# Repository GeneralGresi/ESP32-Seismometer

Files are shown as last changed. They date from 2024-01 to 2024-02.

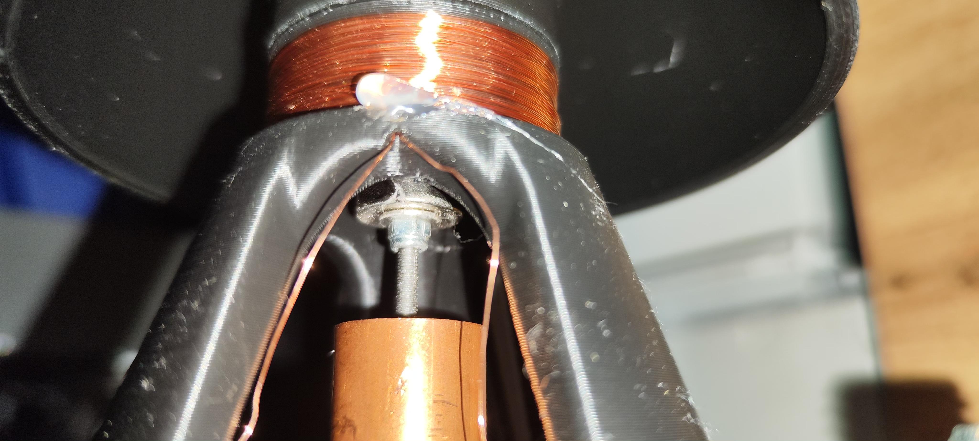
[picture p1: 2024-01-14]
Pictures/Magnet Base.jpg

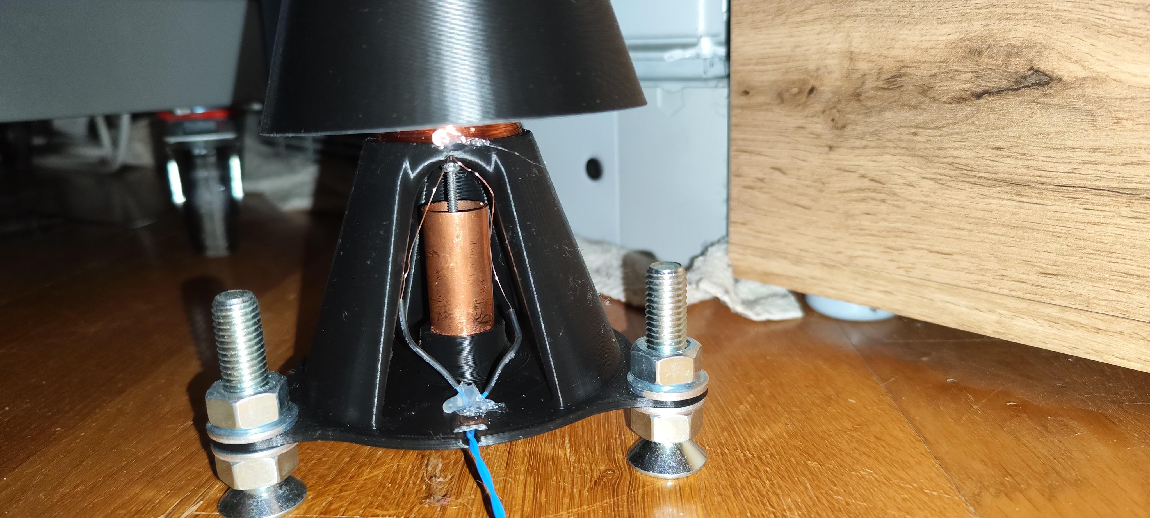
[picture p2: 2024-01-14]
Pictures/Magnet Base 2.jpg

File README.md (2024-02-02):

This is a DIY Project for building a simple 3D Printable Seismometer, interfacing to InfluxDB/Grafana via an ESP32.

POC:
Recorded a quake, Richter 4.5, about 130km away

https://www.zamg.ac.at/cms/de/geophysik/erdbeben/aktuelle-erdbeben/karten-und-listen/bebendetails/austria/quakes/evid53139145



The main principal is a magnet on a spring. Each "movement" will cause the magnet to swing, therefore inducing a voltage/current in a coil. 


Schematic Seismometer Stand

As the coil itself would not produce much voltage, we have to amplify this voltage. Depending on the strength of a potential earthquake I was unsure which gain is needed.
Therefore I disigned a multi gain op-amp circuit utilizing high precision LN1677 chips. This implements a gain of 10, 100 and 1000. Each gain is funneled seperately to an Analog Input pin on the ESP32.



The op-amp circuit works as follows: Via a voltage devider we create a median voltage between 0 and 3.3V. The coil is connected directly to this voltage devider, as well as to each inverting input of the op amps.
The difference between the median voltage and the input voltage is then amplified by the respective gain, creating a bigger offset value.

Circuit

The ESP32 reads these values, funnels it through a software low-pass filter of 35 Hz (Earth Quakes are usually between 0.1Hz and 30Hz, I also want to filter out the mains voltage of 50Hz, therefore everything below 35Hz is considered acceptable).
As due to unknown reasons (at least for me), we are not perfectly centered to 0 during no movement of the magnet, therefore we take the average of 500 readings (at a sample rate of about 200Hz/~5000ys delay between reading we have an average of 2,5 Seconds). 
This average then is used to move the raw median value to 0. This approach works pretty well.

I mapped the min and max values from -1000 to 1000 for each input. If we overshoot this value at for example the X1000 value, we use the next-lowest beeing X100, and multiply it by 10, to get consistent values to InfluxDB.
A value of 300 on the X100 Gain Input will be transmited as 3000 to InfluxDB. The same applies for X10/X100.
The final value then get's put into a queue, as well as the current timestamp. 

I use NTP for time synchronisation - we can't use the server timestamp, as we never send data right away.
The values are first put into a Queue and send the to InfluxDB in batches by a seperate thread.
This ensured, the wifi send command doesn't interrupt further reading of new values. 

For winding of the coil, there is a separate script for an Arduino Uno (or whatever microcontroller), which uses magnets and a magnet switch to register each rotation and display it on an LCD. Serial Printing the value would also be an option though.
The magnet switch is connected to a cordless drill, the Base is connected via a Metric Screw, and a 3D printed adapter. Use about 300-500 windings. More windings = Increased sensitivity.
CoilWinding

The magnetic part of the seismometer looks as follows: It uses 15mm and 10mm Magnets, as well as a 5mm steel threaded rod and some fixation rings with setscrews.
Magnet Part
Magnet on Spring

The upper two magnets are inducing the voltage into the coil, the bottom two are for dampening the movement. Therefore a copper tube with 20mm (inner 18mm) in diameter is inserted into the base.
Base Prototype

Due to eddy currents, the copper tube acts like a dampener/break for the magnets, slowing them down. This greatly shortens swinging after an event.
Using the 3D printed Setscrew, the contraption is lowered into the base, making sure the bigger magnets are perfectly centered within the coil, and the dampening magnets are reaching the copper tube. 
They should be at least 1cm within the tube, in order to have the dampening work even when a swinging motion has the contraption in it's highest position.
This can take some time fiddling around, testing longer or shorter steel rods, and cutting the spring to length. I can't give you any exact numbers, as this depends greatly on the weight of each component.

Magnet Base

Once finished it should look like that:
Magnet Base 2

On the Edges there are M16 Screws and nuts to level the Seismometer. For increased sensitivity, steel threaded Rods which are hammered into the ground can be used.  
For leveling, take a look into each side hole of the base, and make sure the magent contraption is perfectly centered. If it is off, or even worse, it rubs against the copper tube, the reading will be absolutely garbage.

Once you are finished, carefully slíde over and scrow on the conver over the base. This prevents air movement to cause any distortion.

Regarding the circuit:
I enhoused it in a plastic box, with a buck converter which is creating a steady 5V, a Li-Ion module to serve as UPS, as well as some additional capacitors and a choke to smooth the input voltage even more.

Circuit Box

End result:


Why the aluminium foil one may ask? I don't think it helps much, but the intention was the keep external electical signals away from the coil... 

As the ESP32 sends it's data directly to an InfluxDB Instance, we can read out the values via Grafana very easily. Just make sure the timespan is not too big, as we have about 12k values each minute.

On Idle:
Screenshot Grafana Idle

Walking by:


Zoomed in:


As you can see, the dampening can be improved still, however, I consider this a great success.

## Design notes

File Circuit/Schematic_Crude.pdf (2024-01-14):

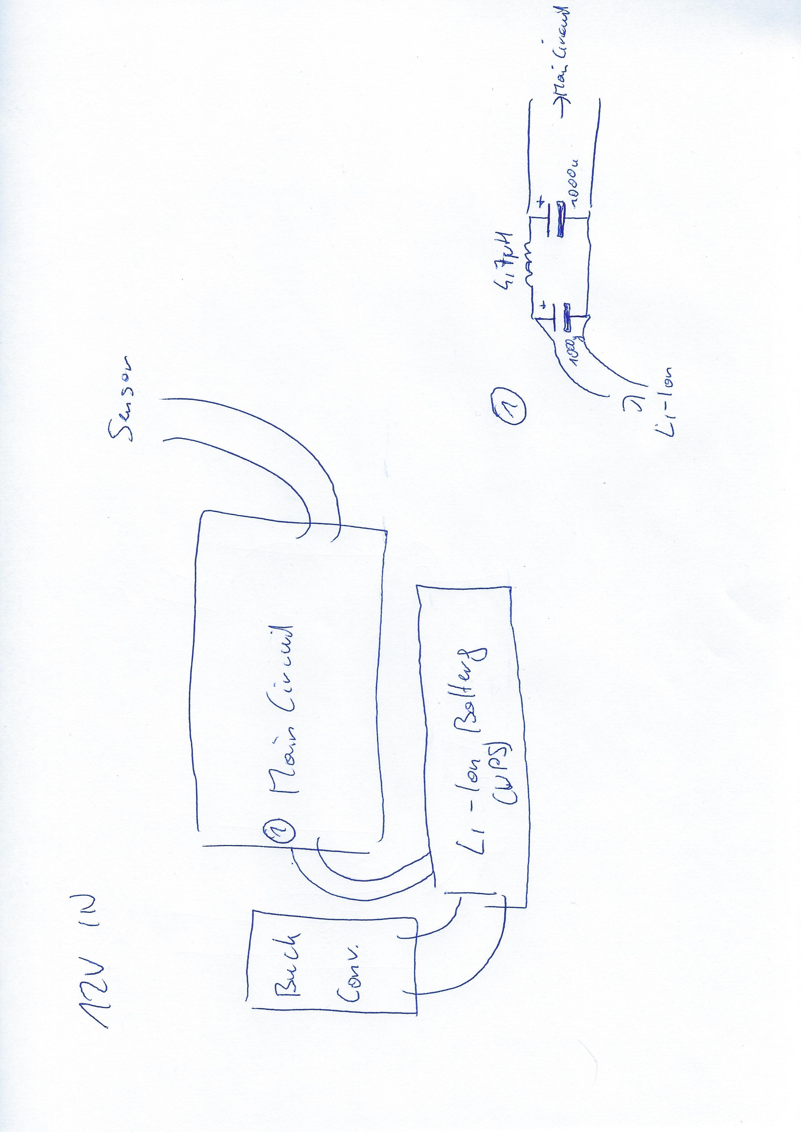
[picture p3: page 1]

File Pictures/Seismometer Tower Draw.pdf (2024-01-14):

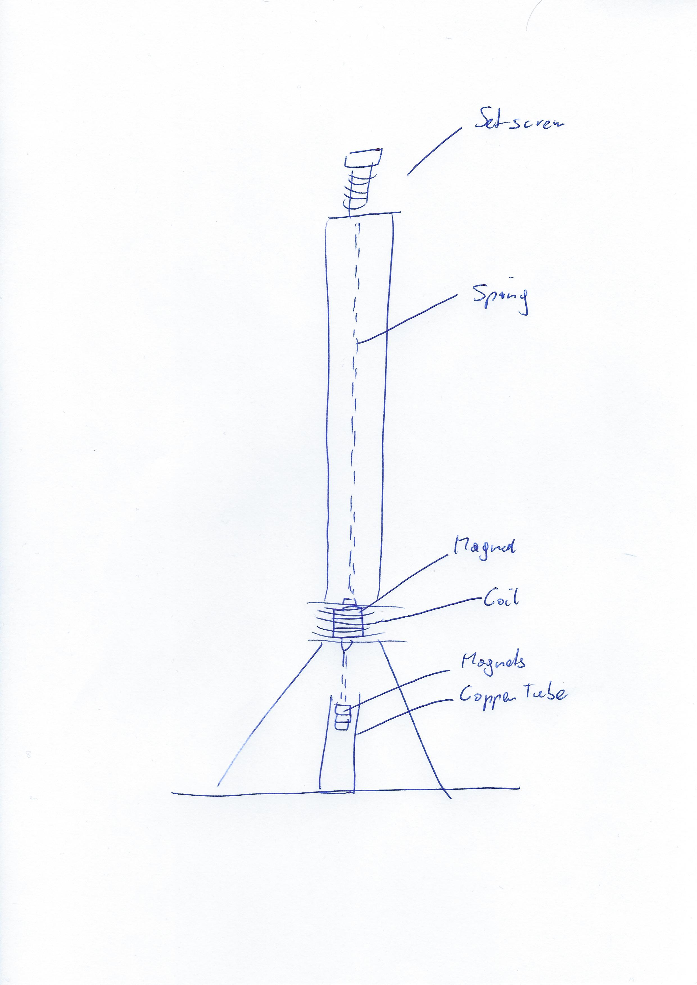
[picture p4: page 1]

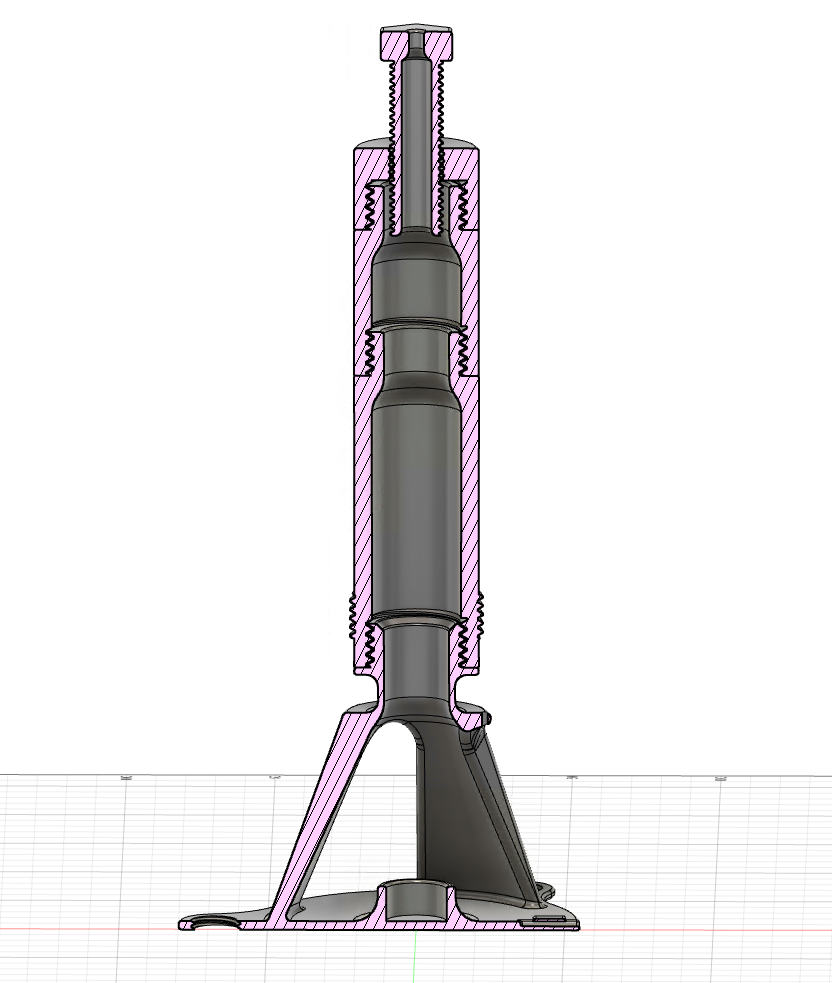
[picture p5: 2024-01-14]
Pictures/Schematic Seismometer Stand.png

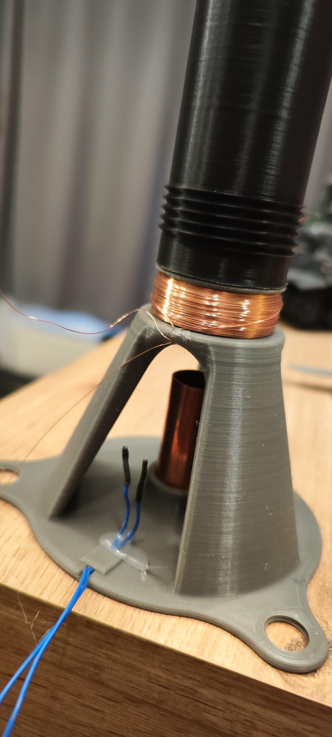
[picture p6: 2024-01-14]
Pictures/Base Prototype 2.jpg

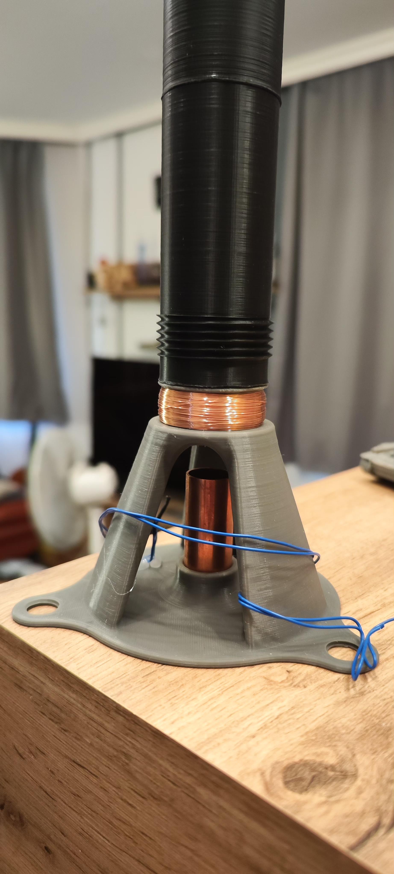
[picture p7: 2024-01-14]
Pictures/Base Prototype.jpg

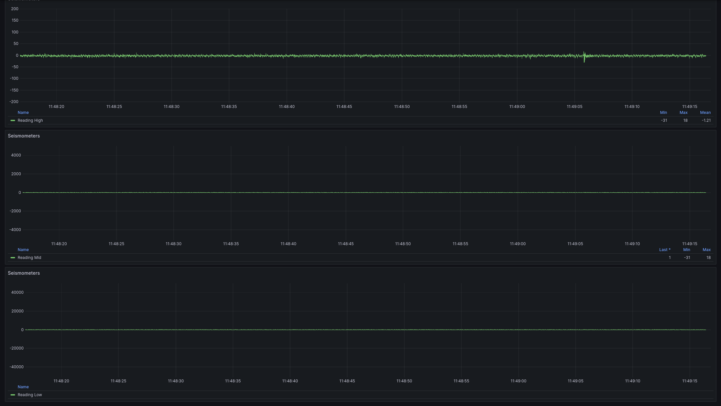
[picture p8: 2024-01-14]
Pictures/Screenshot Grafana Idle.png

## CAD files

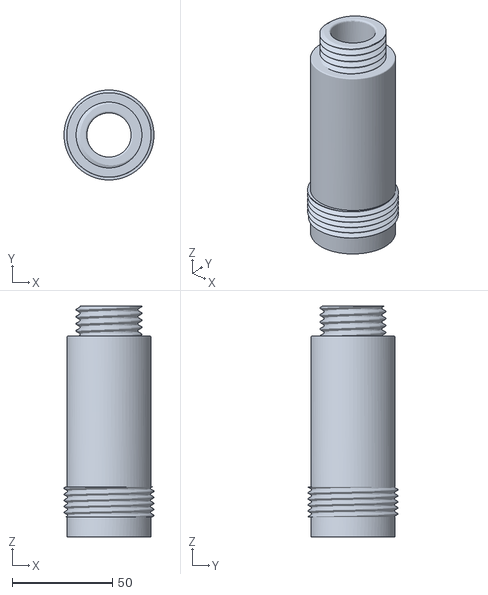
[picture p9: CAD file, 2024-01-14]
STL-Files/Extender 100mm external Thread for Cover.stl
44.8 x 44.8 x 115.0

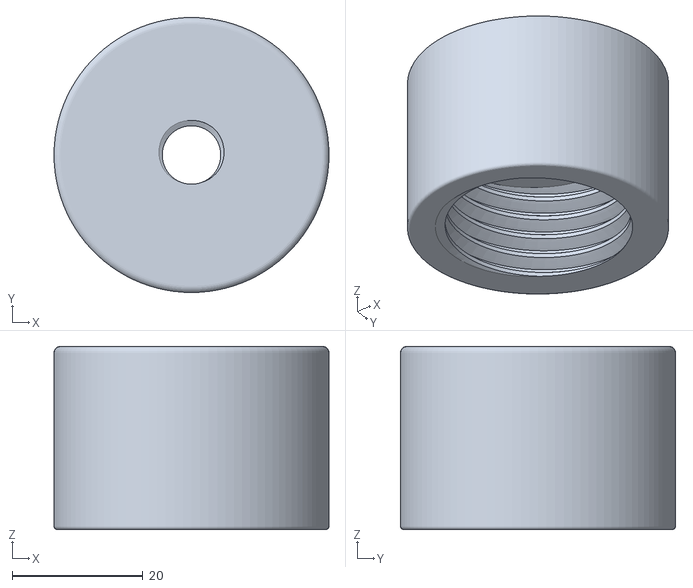
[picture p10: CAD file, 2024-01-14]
STL-Files/Coil Helper.stl
42.0 x 42.0 x 28.0

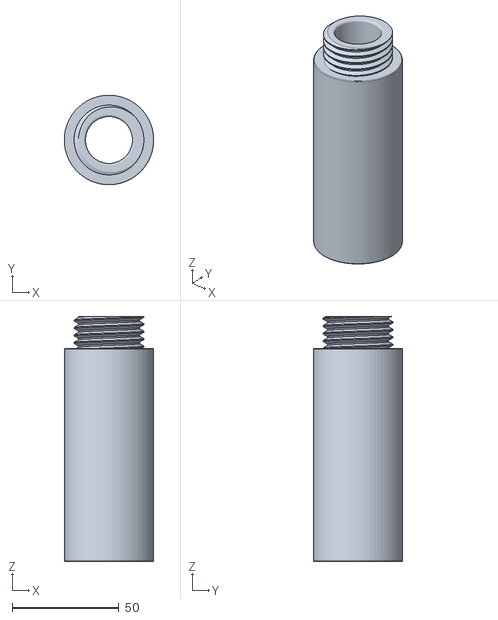
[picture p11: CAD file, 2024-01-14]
STL-Files/Extender 100mm.stl
42.0 x 42.0 x 115.0

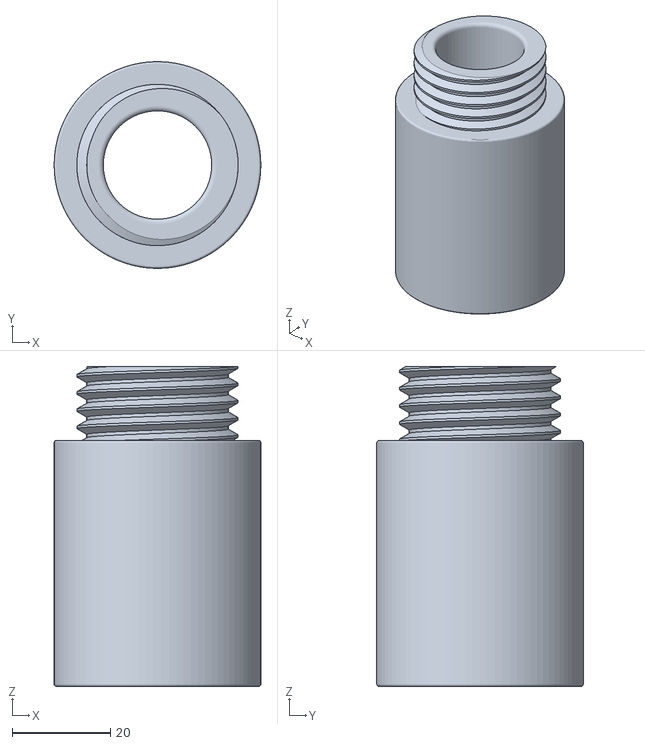
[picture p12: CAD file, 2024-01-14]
STL-Files/Extender 50mm.stl
42.0 x 42.0 x 65.0

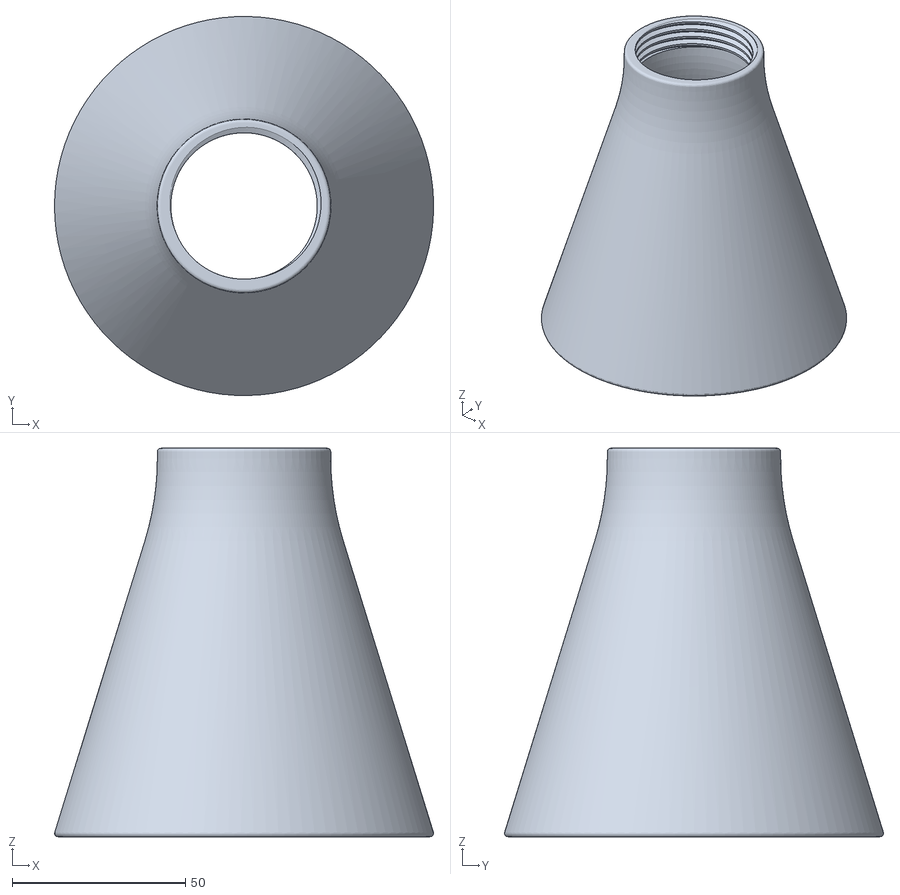
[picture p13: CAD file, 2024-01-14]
STL-Files/Windcover.stl
109.3 x 109.3 x 112.0

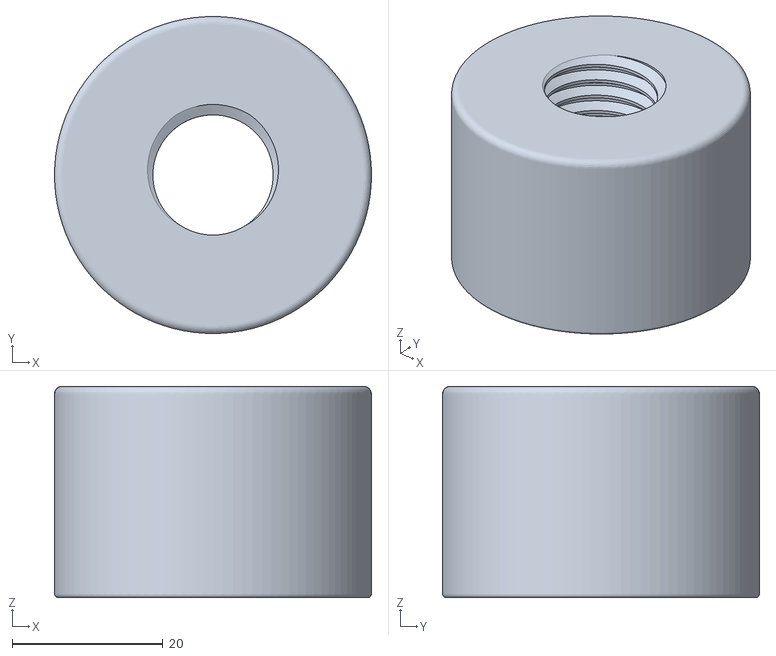
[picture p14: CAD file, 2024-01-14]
STL-Files/Endcap.stl
42.0 x 42.0 x 28.0

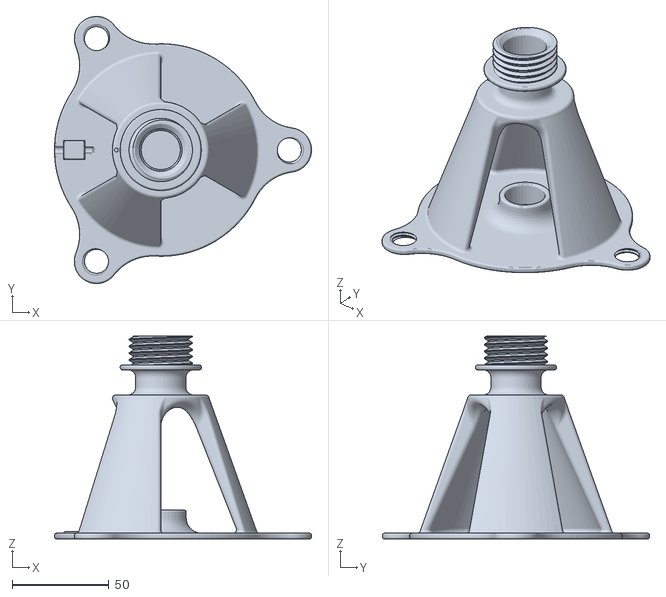
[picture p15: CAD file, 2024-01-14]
STL-Files/Base.stl
132.9 x 138.2 x 105.0

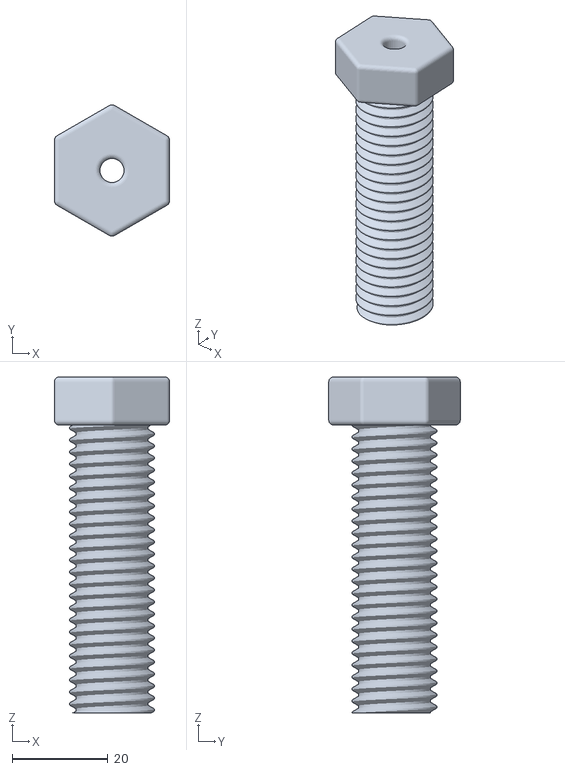
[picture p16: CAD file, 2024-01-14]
STL-Files/Setscrew.stl
24.0 x 27.4 x 70.0

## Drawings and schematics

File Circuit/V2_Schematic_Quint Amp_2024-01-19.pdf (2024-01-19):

5V 19 CLK 20 SD0 21 SD1 22 P15 23 P2 24 P0 25 P4 26 P16 27 P17 28 P5 29 P18 30 P19 31 GND 32 P21 33 RX 34 TX 35 P22 36 P23 37 GND 38

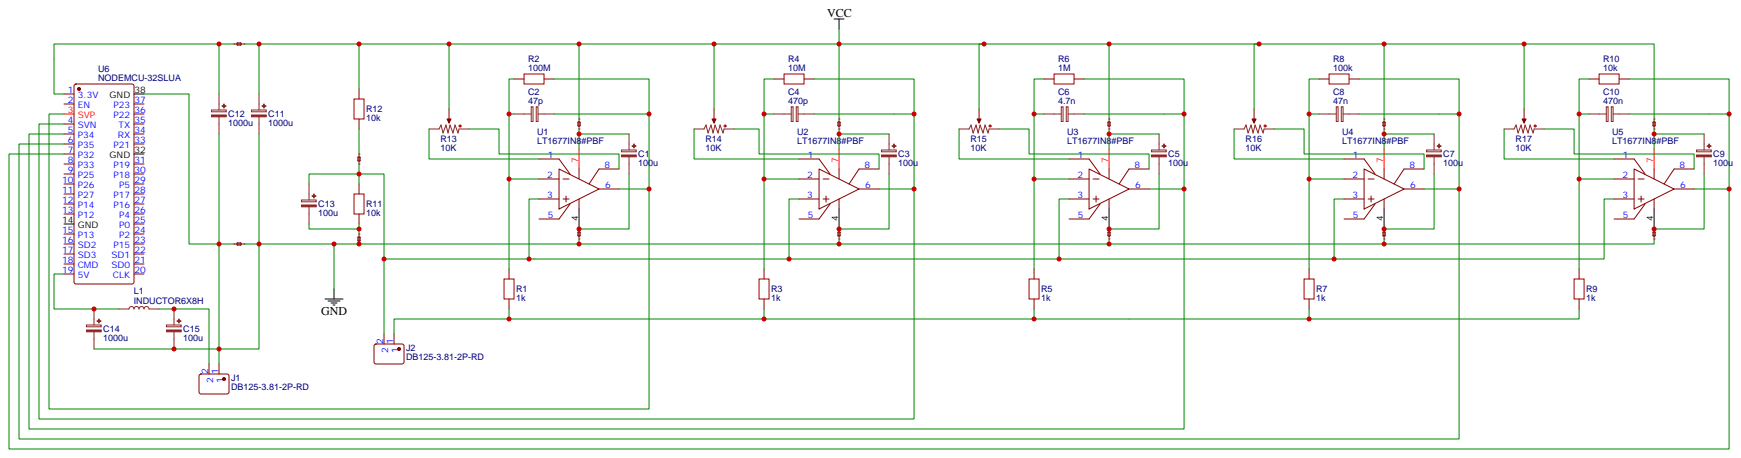
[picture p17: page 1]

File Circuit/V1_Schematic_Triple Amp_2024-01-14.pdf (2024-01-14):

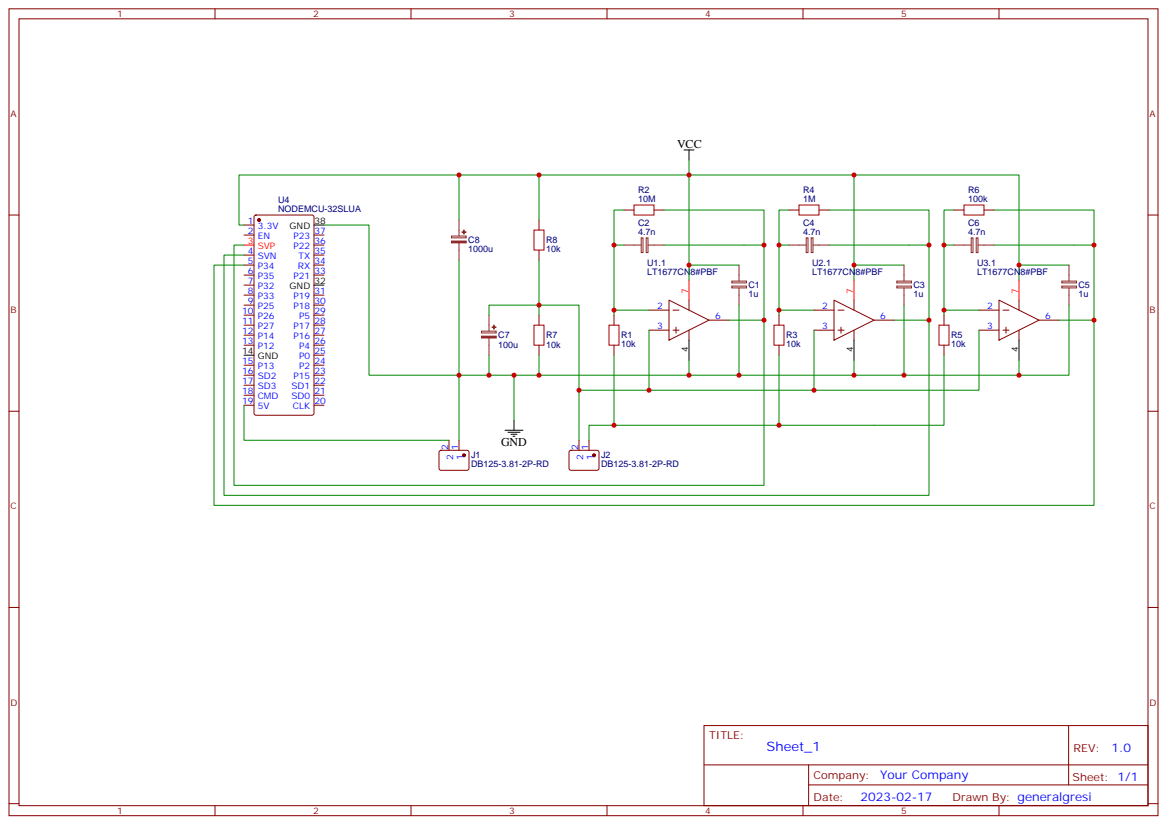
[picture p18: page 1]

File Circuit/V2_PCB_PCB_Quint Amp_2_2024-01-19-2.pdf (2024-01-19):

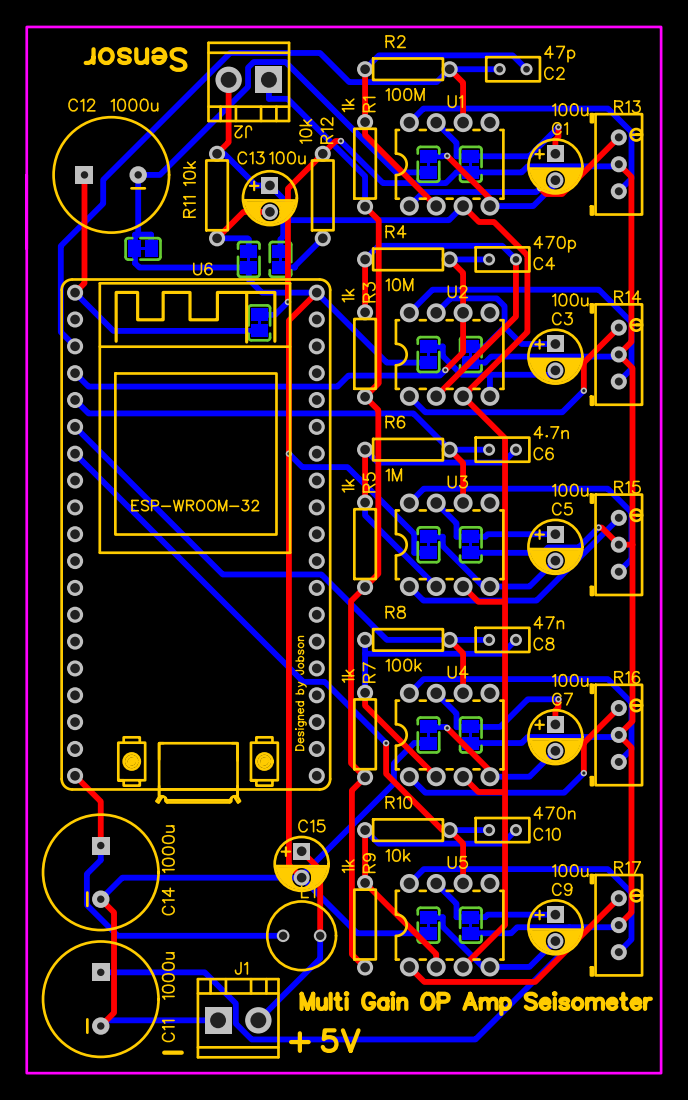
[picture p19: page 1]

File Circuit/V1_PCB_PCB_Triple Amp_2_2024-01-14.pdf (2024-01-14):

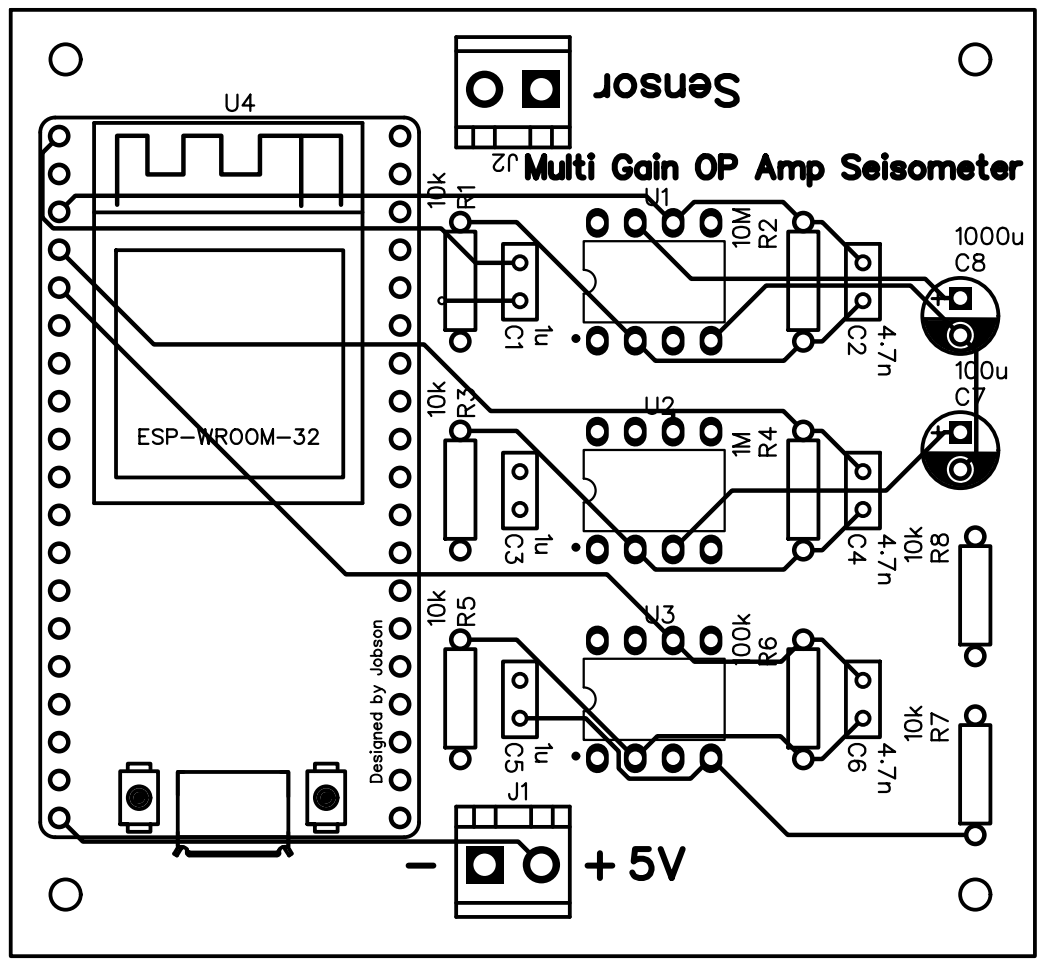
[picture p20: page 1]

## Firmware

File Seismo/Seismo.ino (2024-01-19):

#include <WiFi.h>
#include "credentials.h"
#include <InfluxDbClient.h>
#include "time.h"
#include <esp_task_wdt.h>
#include <WebServer.h>
#include <ElegantOTA.h>
#include "driver/adc.h"
#include "esp_adc_cal.h"
#include <CircularBuffer.h>

#define fwversion "20240116_1658"

#define CUTOFFFREQUENCY 35.0 //in hertz
#define WIFI_RECONNECT_TIMEOUT_S 30
#define TIME_SYNC_INTERVAL_S 300
#define TZ_INFO "CET-1CEST,M3.5.0,M10.5.0/3"

const char* esp_hostname = "ESP32_Seismometer01";
#define DEVICE "Sensor01"


#define inputPinX1000 36
#define inputPinX100 39
#define inputPinX10 34



typedef struct{
   unsigned long long timestamp;
   int value;
}Data;

CircularBuffer<Data,4000> pointBuffer;


float offsetX10 = -75.0;
float offsetX100 = -75.0;
float offsetX1000 = -75.0;

float filteredX10 = 0;
float filteredX100 = 0;
float filteredX1000 = 0;

float PERIOD_READ_US;

unsigned long lastReadTime;
unsigned long lastWriteTime;
unsigned long lastTimeSyncTime;

float alpha; //for lowpass;

TaskHandle_t Task1;
TaskHandle_t Task2;
xQueueHandle xQueue;

esp_adc_cal_characteristics_t adc1_chars;

InfluxDBClient client(INFLUXDB_URL, INFLUXDB_ORG, INFLUXDB_BUCKET, INFLUXDB_TOKEN);
WebServer server(80);

void syncToNTP() {
  if ((unsigned long)(millis() - lastTimeSyncTime) > TIME_SYNC_INTERVAL_S * 1000) {
    timeSync(TZ_INFO, "0.at.pool.ntp.org", "1.at.pool.ntp.org");
    lastTimeSyncTime = millis();
  }
}



void otaSetup() {

  server.on("/", []() {
    server.send(200, "text/plain", "Device: " + String(esp_hostname) + ", Firmware Version: " + String(fwversion) + ", Wifi Signal: " + String(WiFi.RSSI()) + "\n" + 
    "Sample Interval: " + String(PERIOD_READ_US) + ", CUTOFFFREQUENCY: " + String(CUTOFFFREQUENCY) + "\n");
  });
  
  ElegantOTA.setAuth(otaUser, otaPass);
  ElegantOTA.onEnd([](bool success) {
    if (success) {
      Serial.println("OTA update completed successfully.");
      // Add success handling here.
    } else {
      Serial.println("OTA update failed.");
      // Add failure handling here.
    }
  });
  ElegantOTA.begin(&server);
  server.begin();
}

unsigned long lastWifiConnectionAttempt = -WIFI_RECONNECT_TIMEOUT_S * 1000; //don't delay first connection attempt
bool printedWifiInfo = false;
bool ntpSynced = false;
void setupWifi() {
  if (WiFi.status()!= WL_CONNECTED) {
    if ((unsigned long)(millis() - lastWifiConnectionAttempt) > WIFI_RECONNECT_TIMEOUT_S * 1000) {
      printedWifiInfo = false;
      Serial.print("Connecting to ");
      Serial.println(WIFI_SSID);
      
      WiFi.mode(WIFI_STA);
      WiFi.hostname(esp_hostname);
      WiFi.begin(WIFI_SSID, WIFI_PASSWORD);
    
      Serial.println();
  
      lastWifiConnectionAttempt = millis();
    }
  } else {
    if (!printedWifiInfo){
      Serial.println("Wi-Fi Connected");
      Serial.println("IP address: ");
      Serial.println(WiFi.localIP());
      timeSync(TZ_INFO, "0.at.pool.ntp.org", "1.at.pool.ntp.org");
      ntpSynced = true;
      printedWifiInfo = true;
    }
  }
}

void setup() {
  Serial.begin(500000);
  setupWifi();
  otaSetup();
  float sampleFrequency =  float(CUTOFFFREQUENCY) * 4.0;
  PERIOD_READ_US = ((1.0/float(sampleFrequency)) * 1000.0 * 1000.0); //Reading period microseconds


  float tau = 1.0 / (2.0 * PI * (float)CUTOFFFREQUENCY);
  float readPeriodInSeconds = PERIOD_READ_US / 1000.0 / 1000.0;
  alpha = readPeriodInSeconds / (readPeriodInSeconds + tau); 
  
  adc1_config_width(ADC_WIDTH_BIT_12);
  adc1_config_channel_atten(ADC1_CHANNEL_6, ADC_ATTEN_DB_11);
  esp_adc_cal_characterize(ADC_UNIT_1, ADC_ATTEN_DB_11, ADC_WIDTH_BIT_12, 0, &adc1_chars);
  
  xQueue = xQueueCreate(1000, sizeof(Data));

 
  client.setHTTPOptions(HTTPOptions().connectionReuse(true));
  client.setWriteOptions(WriteOptions().writePrecision(WritePrecision::MS).batchSize(50).useServerTimestamp(false));
  
  lastReadTime=micros();
  lastTimeSyncTime = lastWriteTime = millis();

  esp_task_wdt_init(10, true); 

  
  xTaskCreatePinnedToCore(
      dataToQueue, /* Function to implement the task */
      "ReadDataToQueue", /* Name of the task */
      10000,  /* Stack size in words */
      NULL,  /* Task input parameter */
      0,  /* Priority of the task */
      &Task1,  /* Task handle. */
      0); /* Core where the task should run */

  
  xTaskCreatePinnedToCore(
      postToInflux, /* Function to implement the task */
      "postToInflux", /* Name of the task */
      10000,  /* Stack size in words */
      NULL,  /* Task input parameter */
      2,  /* Priority of the task */
      &Task2,  /* Task handle. */
      1); /* Core where the task should run */
  
}


void dataToQueue( void * parameter) {
  esp_task_wdt_add(NULL);
  const TickType_t xTicksToWait = pdMS_TO_TICKS(100);
  BaseType_t xStatus;
  Data dataPoint;
  while (true) {
    esp_task_wdt_reset();
    if (!ntpSynced) {
      
      continue;
    }
    if ((unsigned long)(micros() - lastReadTime) >= PERIOD_READ_US * 0.95) {
      unsigned long delayLeft = PERIOD_READ_US - (micros() - lastReadTime);
      if (delayLeft < PERIOD_READ_US) {
        delayMicroseconds(delayLeft);
      }
      dataPoint.timestamp = getMillis();
      int inputValue = int(readInputs());
      lastReadTime = micros();  
      
      //Serial.println(inputValue);
      dataPoint.value = inputValue;
      xStatus = xQueueSendToBack( xQueue, &dataPoint, xTicksToWait );
    }
  }
}


unsigned long long getMillis() {
  struct timeval tv;
  gettimeofday(&tv, NULL);
  return ((unsigned long long)((tv.tv_sec * 1000LL) + (tv.tv_usec / 1000LL)));
}


float mapfloat(float x, float in_min, float in_max, float out_min, float out_max) {
  return (x - in_min) * (out_max - out_min) / (in_max - in_min) + out_min;
}


float mapOutMiddle(float middle, float value) {
  if (value <= middle) {
    return mapfloat(value, -1000.0, middle, -1000.0 , 0.0);
  } else {
    return mapfloat(value, middle, 1000.0, 0.0, 1000.0);
  }
}

float cutOffFilter(float raw, float filteredValue) {
  return (float)alpha * (float)raw + (float)(1.0 - alpha) * (float)filteredValue;
}

float readInputs() {
  float x1000  =  mapfloat(float(adc1_get_raw(ADC1_CHANNEL_0)),0.0,4095.0,-1000.0,1000.0);
  x1000 = cutOffFilter(x1000, filteredX1000);
  filteredX1000 = x1000;
  x1000 = mapOutMiddle(offsetX10,x1000); 


  
  float x100   =  mapfloat(float(adc1_get_raw(ADC1_CHANNEL_3)),0.0,4095.0,-1000.0,1000.0);
  x100 = cutOffFilter(x100, filteredX100);
  filteredX100 = x100;
  x100 = mapOutMiddle(offsetX100,x100); 


  float x10    =  mapfloat(float(adc1_get_raw(ADC1_CHANNEL_6)),0.0,4095.0,-1000.0,1000.0);
  x10 = cutOffFilter(x10, filteredX10);
  filteredX10 = x10;
  x10 = mapOutMiddle(offsetX1000,x10); 

  if (x1000 >= 750 || x1000 <= -750) {
    if (x100 >= 750 || x100 <= -750) {
      return x10*100.0;
    } else {
      return x100*10.0;
    }
  } else {
    return x1000;
  }
}


void postToInflux(void * parameter) {
  esp_task_wdt_add(NULL);
  const TickType_t xTicksToWait = pdMS_TO_TICKS(2);
  BaseType_t xStatus;

  while(true) {
    esp_task_wdt_reset();
    syncToNTP();

    setupWifi();
    otaLoop();
    
    Data dataPoint;
    
    xStatus = xQueueReceive( xQueue, &dataPoint, xTicksToWait );
    while(xStatus == pdPASS) {
      esp_task_wdt_reset();
      pointBuffer.push(dataPoint); //we send it from the queue to a circular buffer, so we can fifo
      xStatus = xQueueReceive( xQueue, &dataPoint, xTicksToWait );
    }
    //Serial.println("Pointbuffer Size: " + String(pointBuffer.size()));

    while (!pointBuffer.isEmpty() && WiFi.status()== WL_CONNECTED) {
      esp_task_wdt_reset();
      Data dataPoint = pointBuffer.first();
      Point seismoPoint("Seismometer");
      seismoPoint.addTag("device", DEVICE);
      seismoPoint.addField("reading", dataPoint.value);
      seismoPoint.setTime(dataPoint.timestamp);

      //Serial.print("Writing: ");
      //Serial.println(seismoPoint.toLineProtocol());
      if (!client.writePoint(seismoPoint)) {
        Serial.print("InfluxDB write failed: ");
        Serial.println(client.getLastErrorMessage());
        break;
      } else {
        pointBuffer.shift(); //only on success shift it.
      }
    }
  }
}

void otaLoop() {
  server.handleClient();
  ElegantOTA.loop();
}


void loop() {
  esp_task_wdt_reset();
  delay(10);
}

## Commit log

2024-01-14 Added periodic timesync, mitigate millis() and micros() overflow, multicore Influx-Push
2024-01-14 No threading
2024-01-14 Milliseconds is enough!
2024-01-14 Calibration, Moving Average, Smoothing
2024-01-14 Correct Server, increase window for moving avg, Serial print Data
2024-01-14 Removed prints
2024-01-14 Add Software lowpass filter
2024-01-14 Increase sample frequency
2024-01-14 Revert "Increase sample frequency"
    This reverts commit d875928b19b5f7ed192db55a6870616d64db44a1.
2024-01-14 Added 3D Printable STL Files
    [Base.stl, Coil Helper.stl, Endcap.stl, Extender 100mm external Thread for Cover.stl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]
2024-01-14 Added circuit diagrams
2024-01-14 Added Coil Counter Arduino Code
2024-01-14 Added circuit drawing
2024-01-19 Circuit and PCB for preperation of Version 2 Add two additional Gains with x10000 and x100000, also fix Capacitor Values for the Low pass filters. Depending on the Feedback Resistor we have to use a 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
